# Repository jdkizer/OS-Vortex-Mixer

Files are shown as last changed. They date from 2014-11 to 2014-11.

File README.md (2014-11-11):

OS-Vortex-Mixer
===============

3D printed vortex mixer

Total cost ~$25 (comercial $125 -$500)

Motor-$6.55 ( http://www.amazon.com/gp/product/B00NN6EXV0/ref=oh_aui_detailpage_o02_s00?ie=UTF8&psc=1)

Micro Switch-$1.82 ( http://www.amazon.com/Momentary-Hinge-Lever-Micro-Switch/dp/B008SO0IGQ/ref=sr_1_6?s=industrial&ie=UTF8&qid=1415685749&sr=1-6&keywords=micro+switch)

Single Pole Tripple Throw-$5.25 Switch (http://www.amazon.com/Position-SP3T-1P3T-Slide-Switch/dp/B008DFYVX6/ref=sr_1_2?s=industrial&ie=UTF8&qid=1415686001&sr=1-2&keywords=sp3t)

Bearing-$3.99 ( http://www.amazon.com/Bearing-Shielded-5x10x4-Miniature-Bearings/dp/B002BB8ZEO/ref=sr_1_1?s=industrial&ie=UTF8&qid=1415686173&sr=1-1&keywords=MR105ZZ )

Power Supply-$6.55 (any 12V source ie. upcycled ATX PSU, or  http://www.amazon.com/JACKYLED-Switching-Power-Supply-Adapter/dp/B006NTNGN0/ref=pd_sim_sbs_indust_1?ie=UTF8&refRID=138A1S1Q5031T6KMM8VG)

Potentiometer-$1.59 (http://www.digikey.com/product-search/en?x=0&y=0&lang=en&site=us&keywords=987-1276-ND+)

LM317-$0.57 (http://www.digikey.com/product-search/en?vendor=0&keywords=LM317TGOS-ND

x2 M5x10 Bolt and nut

Filiment -$3.00

Intructions

1. Assemble electronics acording to schematic
2. Hot Glue micro switch onto post on Vortex_Mixer_Base
3. Hot Glue other electronics into Vortex_Mixer_Base
4. Place motor in the Vortex_Mixer_Clamp, tighten with one bolt and nut.
5. Insert Nut into Vortex_Mixer_Coupler
6. Attatch bearing to Vortex_Mixer_Coupler using second M5 bolt
7. Push Vortex_Mixer_Coupler onto motor shaft
8. Align hinge of Vortex_Mixer_Clamp with Vortex_Mixer_Base and pin with 1.75mm filament.
9. Secure Vortex_Mixer_Lid with Rubber Bands
10. Add either version of Vortex_Mixer_Cap over the bearing

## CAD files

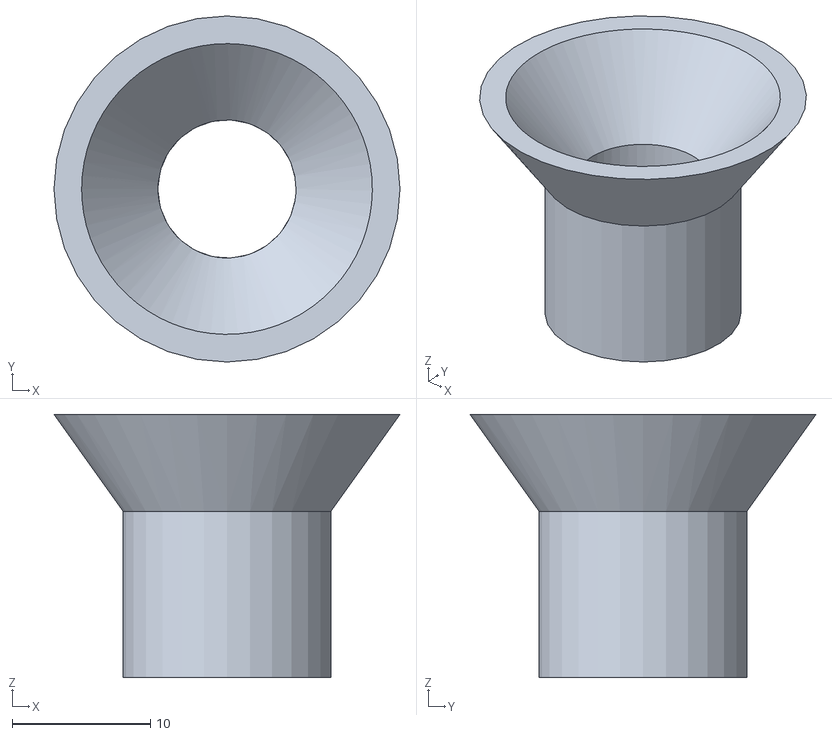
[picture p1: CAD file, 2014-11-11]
Vortex_Mixer_Cap.stl
25.0 x 25.0 x 19.0

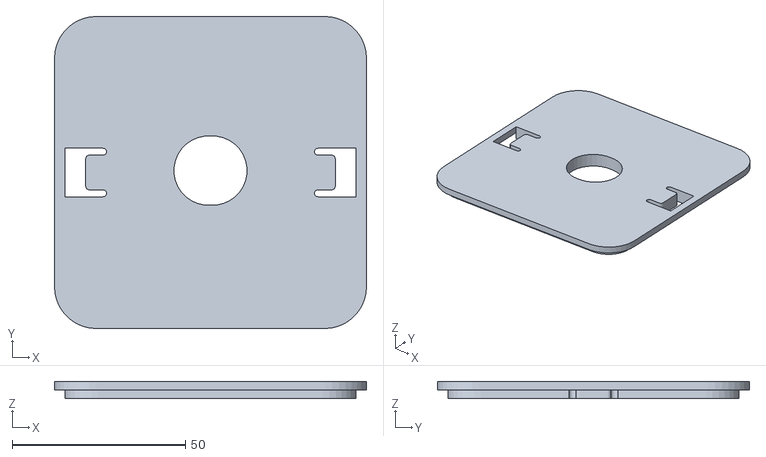
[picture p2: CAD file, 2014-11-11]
Vortex_Mixer_Lid.stl
90.0 x 90.0 x 5.00

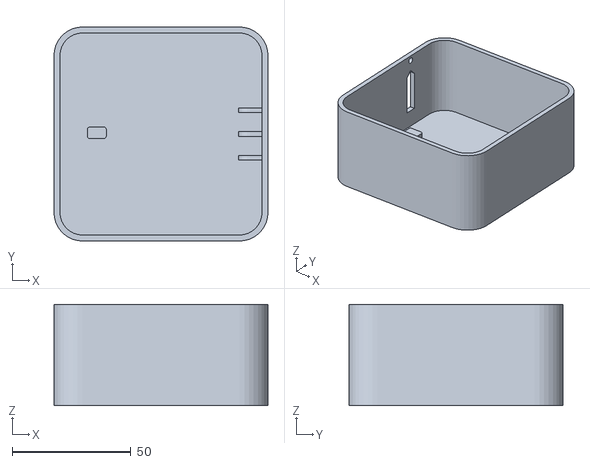
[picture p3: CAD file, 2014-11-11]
Vortex_Mixer_Base.stl
90.0 x 90.0 x 42.5

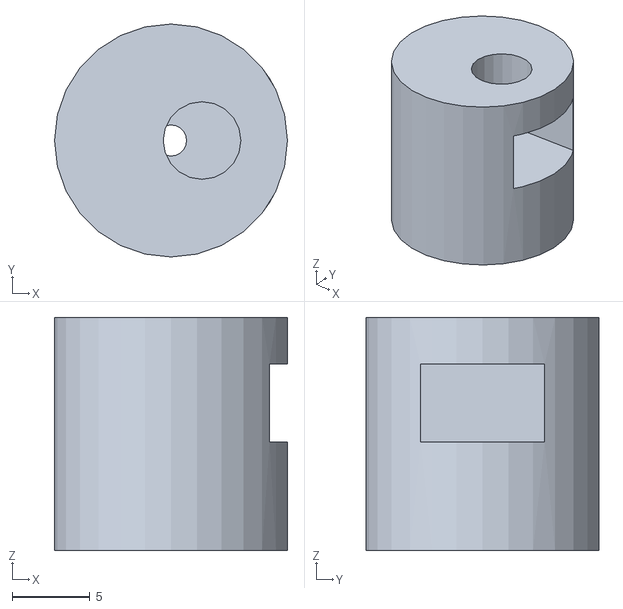
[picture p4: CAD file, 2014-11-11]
Vortex_Mixer_Coupler.stl
15.0 x 15.0 x 15.0

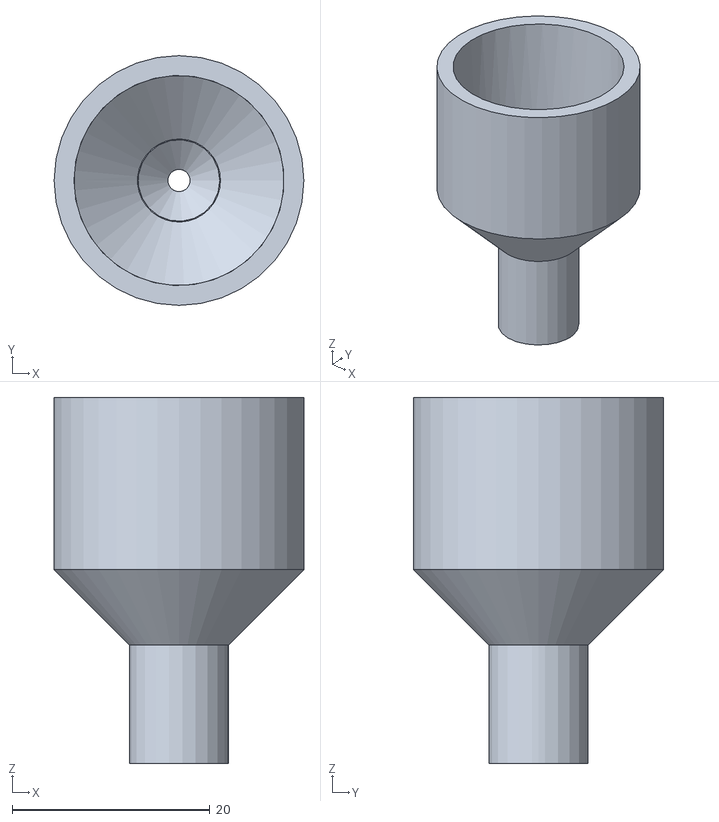
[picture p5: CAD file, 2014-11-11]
Vortex_Mixer_Cap_standalone.stl
25.2 x 25.2 x 37.0

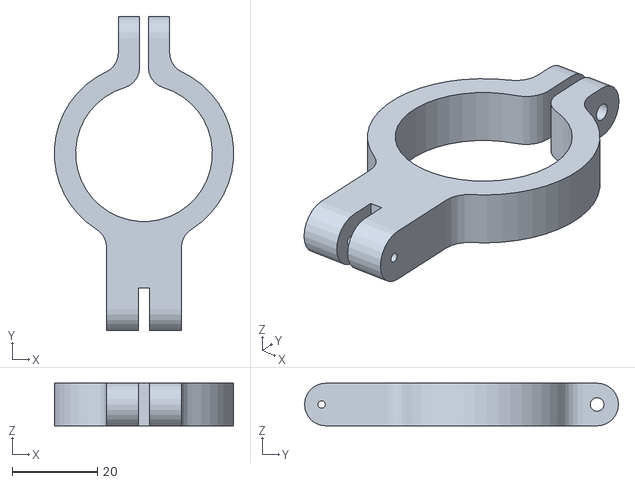
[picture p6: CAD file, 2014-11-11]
Vortex_Mixer_Clamp.stl
41.9 x 73.5 x 10.0

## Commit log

2014-11-11 added cad
    [Vortex_Mixer_0af18736fd07584ba9713a9d165c1caa-Vortex_Mixer_Coupler.stl, Vortex_Mixer_10a84be48c688284e880dff7fb2d1af9-Vortex_Mixer_Clamp.stl, Vortex_Mixer_398b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]
2014-11-11 changed file names
    [Vortex_Mixer_Base.stl, Vortex_Mixer_Cap.stl, Vortex_Mixer_Cap_standalone.stl, Vortex_Mixer_Clamp.stl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]
2014-11-11 Delete Vortex_Mixer_0af18736fd07584ba9713a9d165c1caa-Vortex_Mixer_Coupler.stl
    duplicate
    [Vortex_Mixer_0af18736fd07584ba9713a9d165c1caa-Vortex_Mixer_Coupler.stl]
2014-11-11 Delete Vortex_Mixer_10a84be48c688284e880dff7fb2d1af9-Vortex_Mixer_Clamp.stl
    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
    [Vortex_Mixer_10a84be48c688284e880dff7fb2d1af9-Vortex_Mixer_Clamp.stl]
2014-11-11 Delete Vortex_Mixer_398bba1aa5fa66f2ae49c2ade291ad24-Vortex_Mixer_Cap_standalone.stl
    dulplicate
    [Vortex_Mixer_398bba1aa5fa66f2ae49c2ade291ad24-Vortex_Mixer_Cap_standalone.stl]
2014-11-11 Delete Vortex_Mixer_4319df92697d41f9fcbc2a777679d424-Vortex_Mixer_Lid.stl
    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
    [Vortex_Mixer_4319df92697d41f9fcbc2a777679d424-Vortex_Mixer_Lid.stl]
2014-11-11 Delete Vortex_Mixer_46b86ccf3f9498d9ac006d7b4ac7edf2-Vortex_Mixer_Cap.stl
    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
    [Vortex_Mixer_46b86ccf3f9498d9ac006d7b4ac7edf2-Vortex_Mixer_Cap.stl]
2014-11-11 Delete Vortex_Mixer_6a8d7a5f32520760d442a2ca00f79c3e-Vortex_Mixer_Base.stl
    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
    [Vortex_Mixer_6a8d7a5f32520760d442a2ca00f79c3e-Vortex_Mixer_Base.stl]
